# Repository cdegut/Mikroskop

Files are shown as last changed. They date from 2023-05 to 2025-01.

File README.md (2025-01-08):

# An open-sourced 3D printable microscope with a large CNC stage

[bioRxiv.org](https://www.biorxiv.org/content/10.1101/2024.12.31.630915v1)

Welcome to the repository for an affordable, high-performance, open-source microscope. Designed with researchers in mind, this versatile platform supports brightfield, fluorescence imaging, and high-throughput scanning of standard microtiter plates. It is fully 3D-printable, easy to assemble, and built for customization. Explore the project to access design files, firmware, and software, and join the growing community of users advancing accessible microscopy.

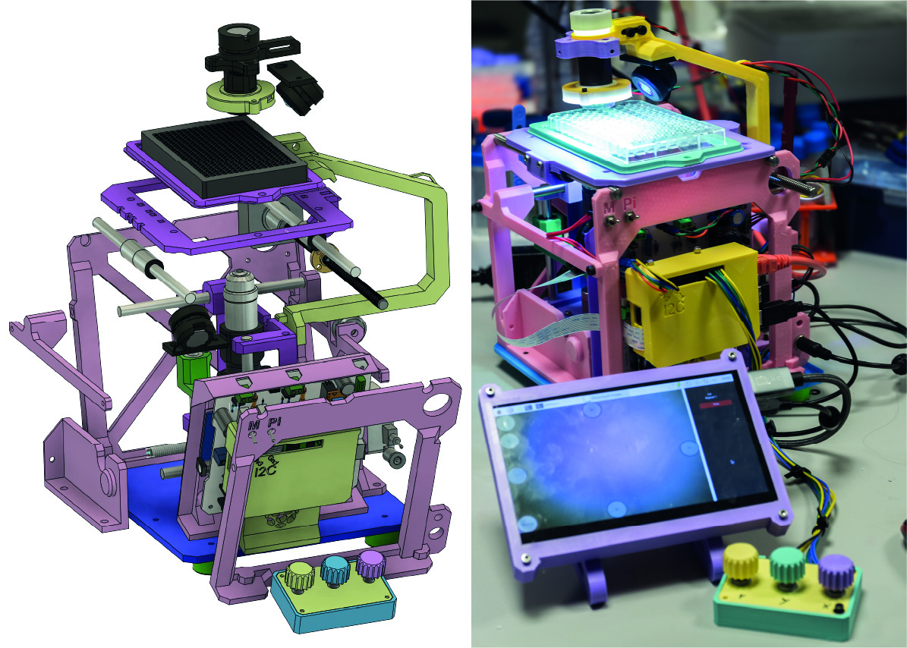
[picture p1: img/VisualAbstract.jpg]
Visual Abstract


A 200um tardigrade, 40x objective with  ring light for oblique illumination and Kristiansen type diffusion (magic tape above the sample!)

YouTube Video (https://www.youtube.com/watch?v=YF4frYpX1ZY)

## Navigation

[Building Instruction](hardware/readme.md)

[Bill of materials](hardware/)

[3D printable Files](hardware/print_files/readme.md)

[Samples images and video](samples)

[Arduino firmware](firmware/readme.md)

[Python sources](modules/readme.md)

Visit Stats

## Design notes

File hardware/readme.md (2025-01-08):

WIP expect everything to be dispnible by the 10th of january

This folder contains all the 3d printable files for building the microscope, with building instruction and some extra information in the readme files.

## Building order

[1 Base](mecanical_stage/base_plate/readme.md)

[2 X Axis](mecanical_stage/X_axis/readme.md)

[3 Optical Stack](optical_stack/readme.md)

[4 Focus Axis](mecanical_stage/Focus_axis/readme.md)

[5 Electronic](electronic/readme.md)

[6 Y Axis](mecanical_stage/Y_axis/readme.md)

[7 Raspberry Pi](raspberryPi/readme.md)

[8 Sample Illumination](mecanical_stage/Y_axis/readme.md)

[9 Sample holders](sample_holders)

## Bill of Materials

Bill Of meterials

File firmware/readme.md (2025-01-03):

# Arduino firmware

This is the arduino firmware, it should be uploaded on an Arduino R4 (minima) using the plateformIO extension for VScode.

## How to

Coming soon

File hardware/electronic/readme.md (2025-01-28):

# Electronic mainboard

The electronic main board mostly serves as an interconnect for off-the-shelf modules Power and control for the motors are managed by Trinamic TMC2209 stepper drivers in a StepStick-compatible format. While it is technically possible to use different drivers, the firmware employs the StallGuard4 feature of the Trinamic drivers for homing the axes. If a different driver is used, end-stop switches will need to be added, and the firmware reconfigured accordingly (not recomeended to try)
The current version 1.2.1 of the mainboard is slighly different from the figures, they will be updated in the coming days.

the gerber zip file contain all that is needed to order the PCB from a manufacturer such as JLCPCB. It is a 2 layer board with 1 oz/sq ft copper.

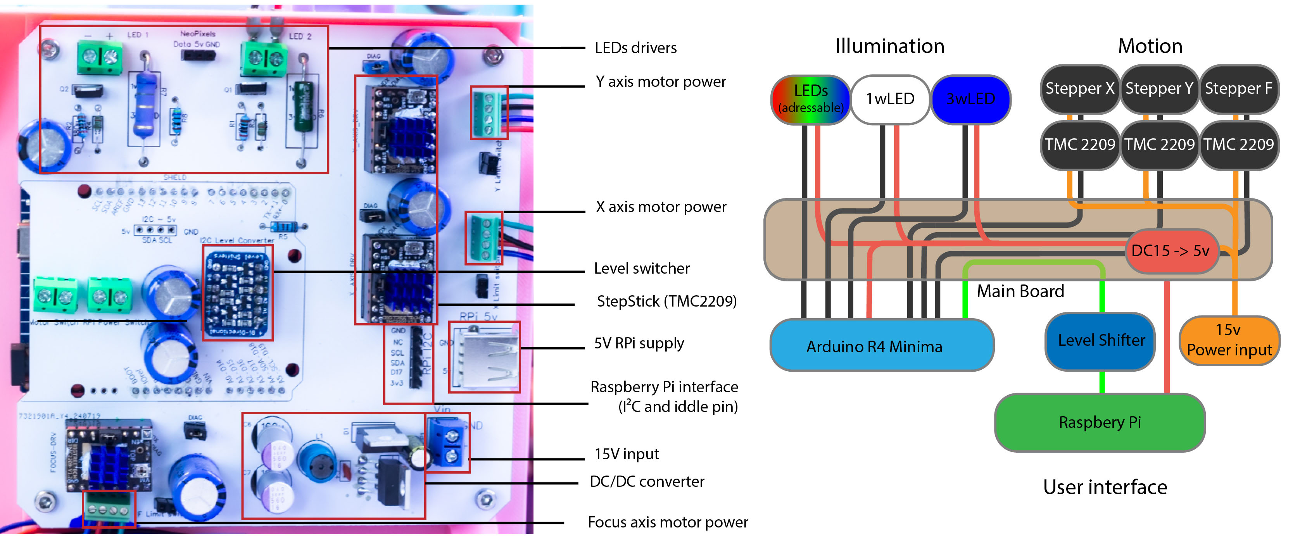
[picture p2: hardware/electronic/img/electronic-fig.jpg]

Photograph of the populated custom PCB and schematic of the interconnections. Red shows power line, black shows transistor to transistor logic (TTL), and green shows the I2C link.

The main printed part for the electronic is the electronic bracket that serve as a mount for all the electronic.
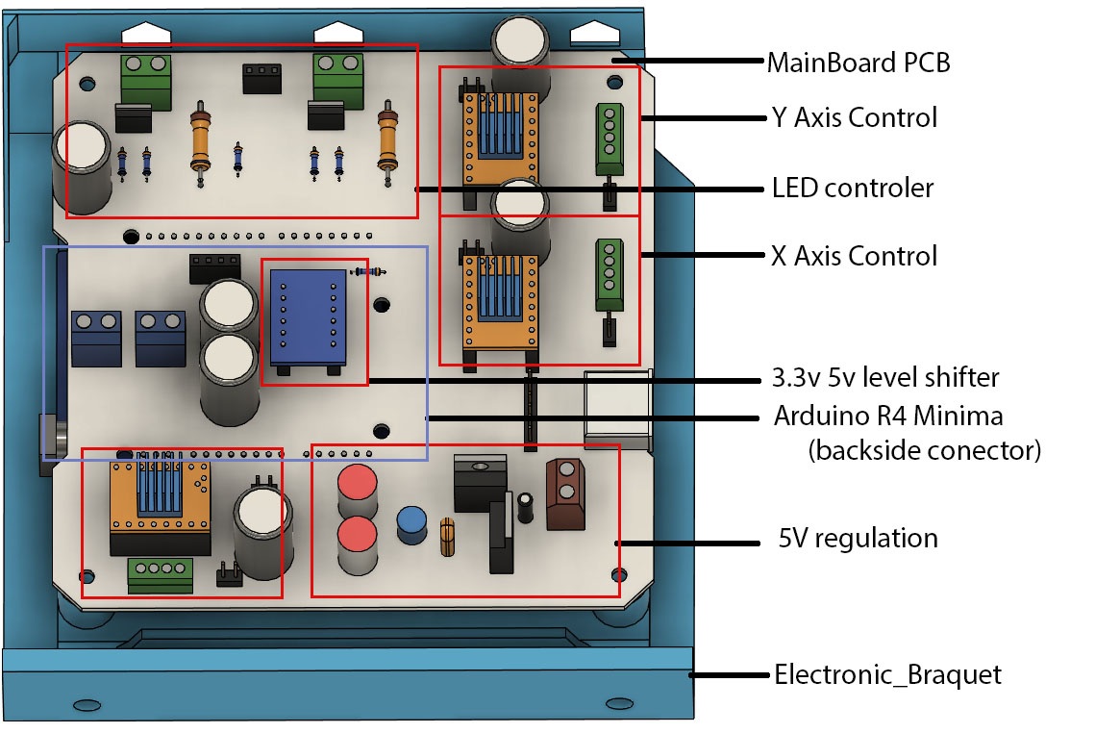
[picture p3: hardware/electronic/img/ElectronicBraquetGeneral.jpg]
General


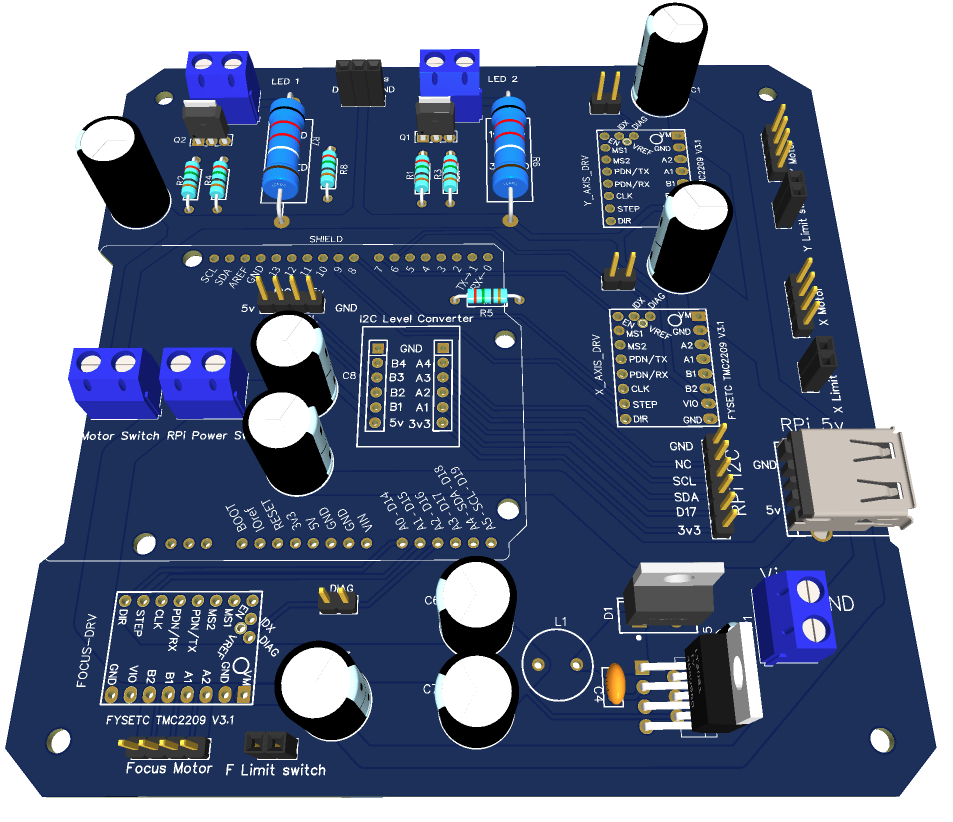
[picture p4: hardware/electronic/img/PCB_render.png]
PCB render

3D render of the PCB

PCB render
PCB Schematics

## Heat set inserts

The bracket requires:

* 2 - M4 ø 6 mm OD heat set insert
* 4 - M3 ø 5 mm OD heat set insert

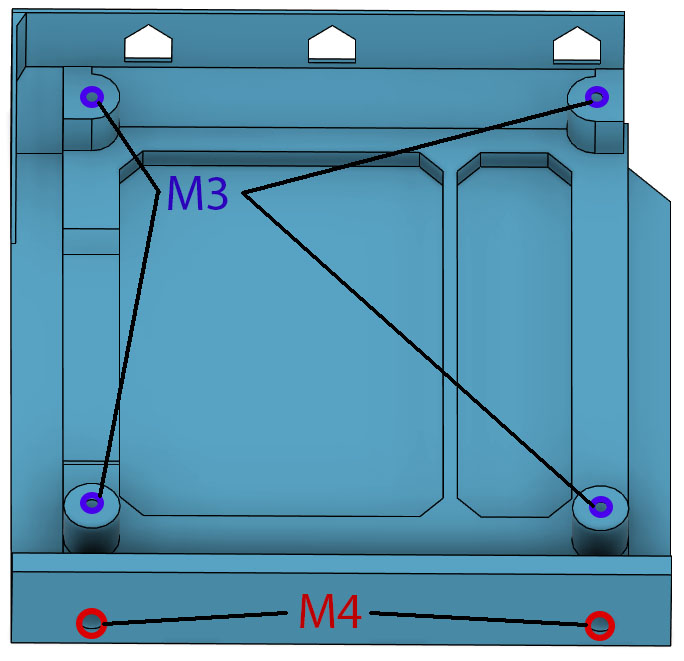
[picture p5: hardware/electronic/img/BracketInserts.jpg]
Inserts


## In Assembly context

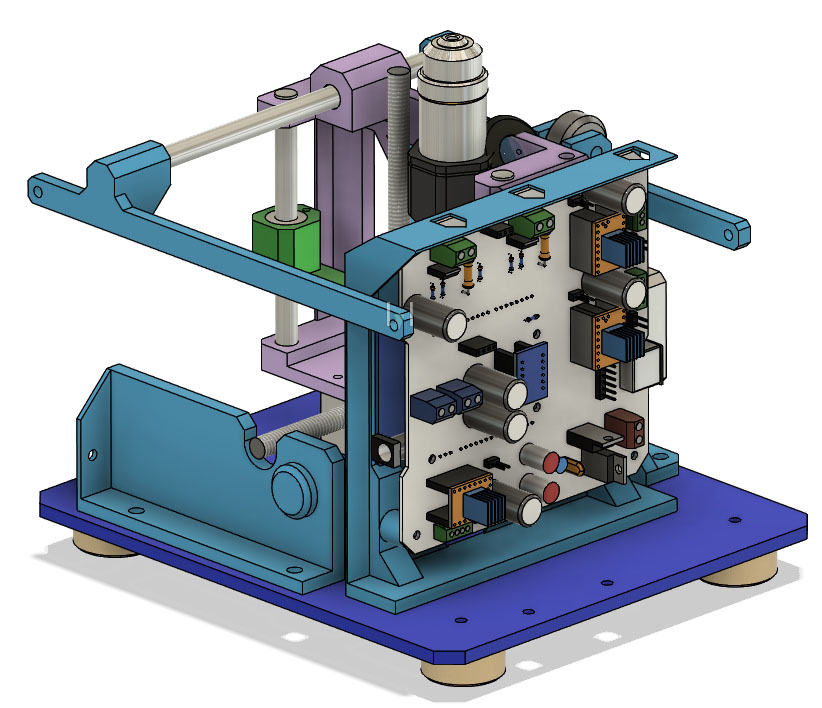
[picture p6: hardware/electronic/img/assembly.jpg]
Assembly


## Connection

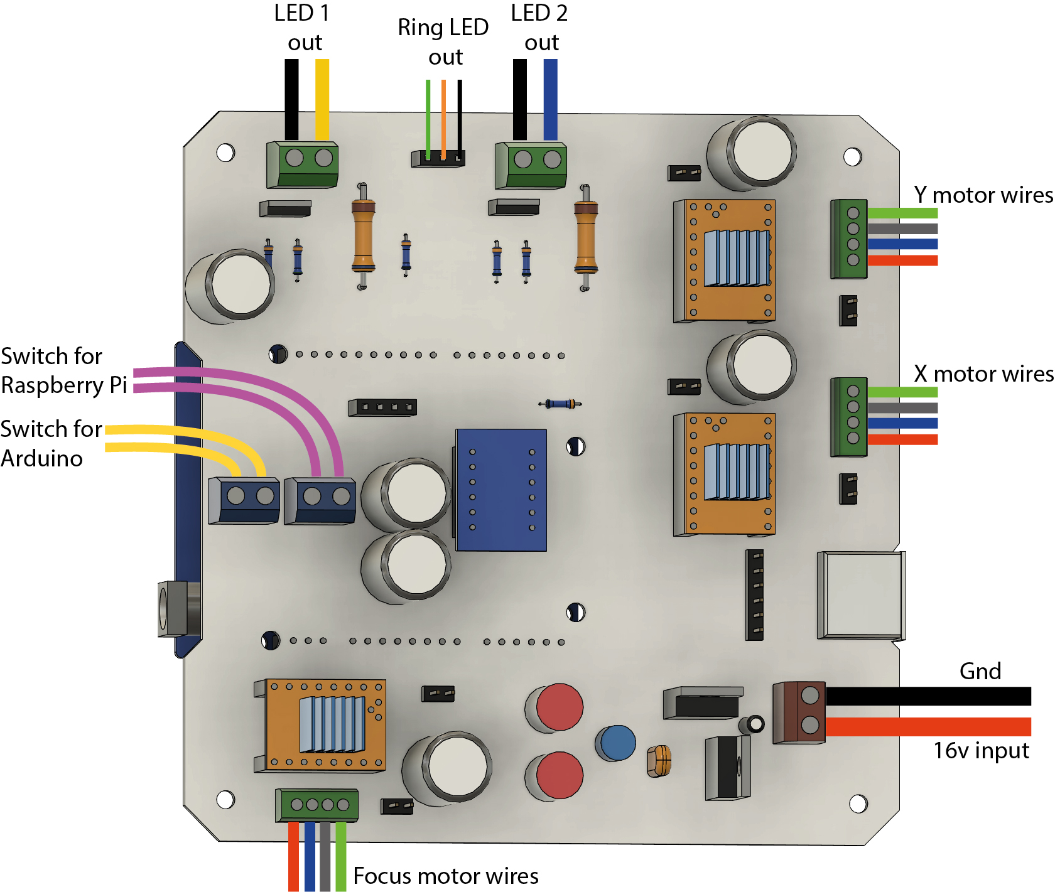
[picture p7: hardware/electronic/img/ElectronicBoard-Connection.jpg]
Connection image


## Alternate power supply

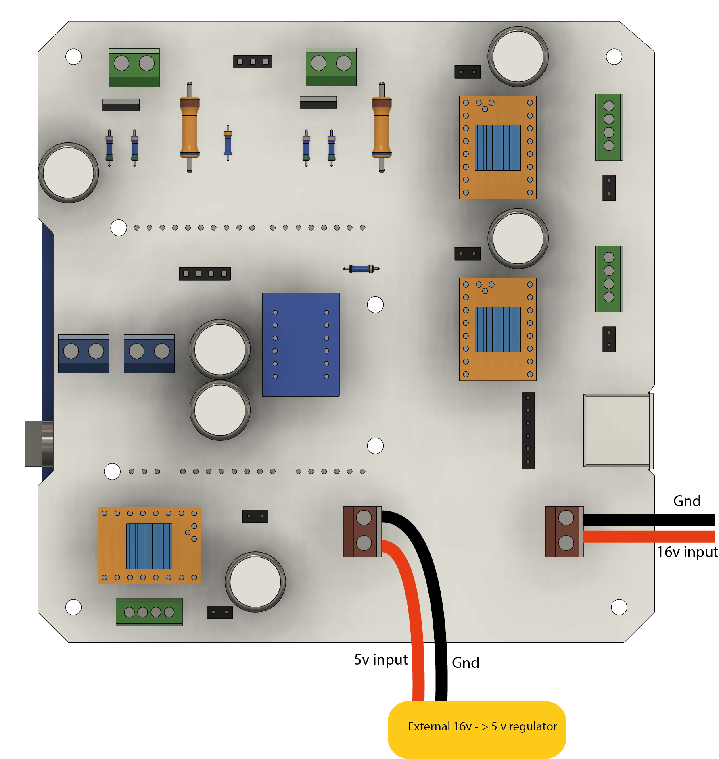
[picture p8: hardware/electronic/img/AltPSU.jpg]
External 5V


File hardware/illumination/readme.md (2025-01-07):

# Illumination system

The top illumination system is all attached to the light_snek , this part can be printed with large layer hight for speed (0.2mm), it is a structural part that should not flexed, therefore it should have >3 walls, and printed with >25% infill.

All the other parts contain threads, and like the optical stack, shopuld be printed with thin layers (<0.1mm), and highest possible quality setting.

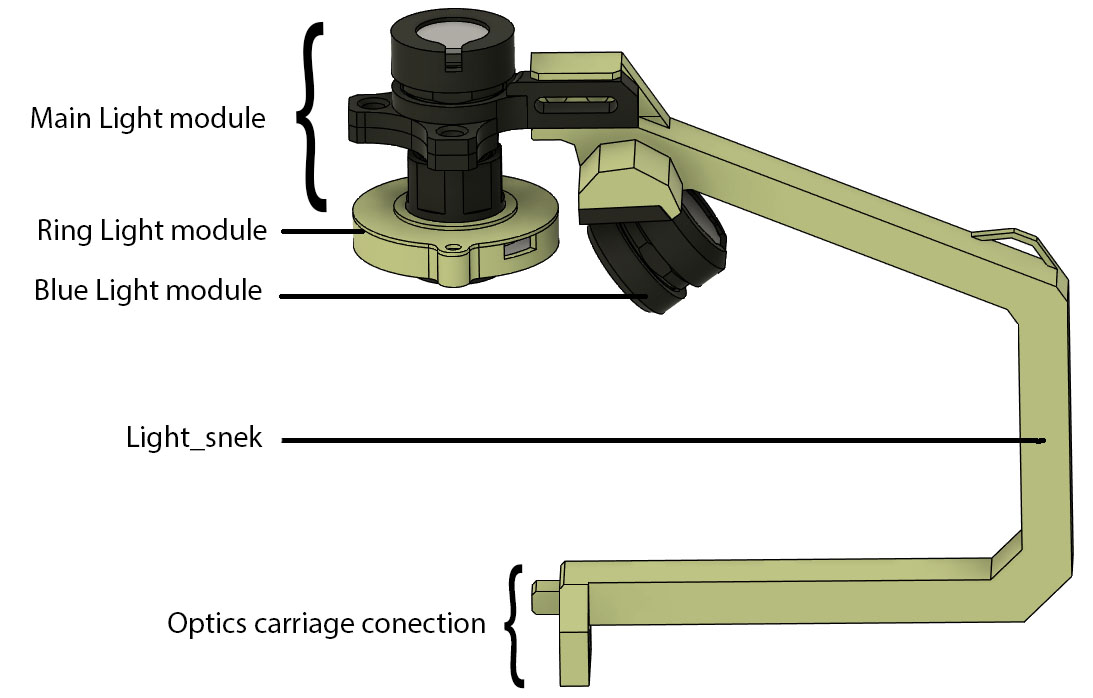
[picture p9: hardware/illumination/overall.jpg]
view of overall top side illumination


## Light Snek

The light snek is the large arm that connect the illumination system to the [optics carriage](../mecanical_stage/Focus_axis/readme.md).

## Illumination component

* [Main light Module](./main_light_module/readme.md)

* [Ring light Module](./ring_light_module/readme.md)

* [Blue light Module](./blue_light_module/readme.md)

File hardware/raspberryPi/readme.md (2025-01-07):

# The RaspberryPi

## Software configuration

[Raspberry Pi Software Configuration](RaspberryPi_config.md)

## Pi Bracket

A pi bracket and cover need to be printed.

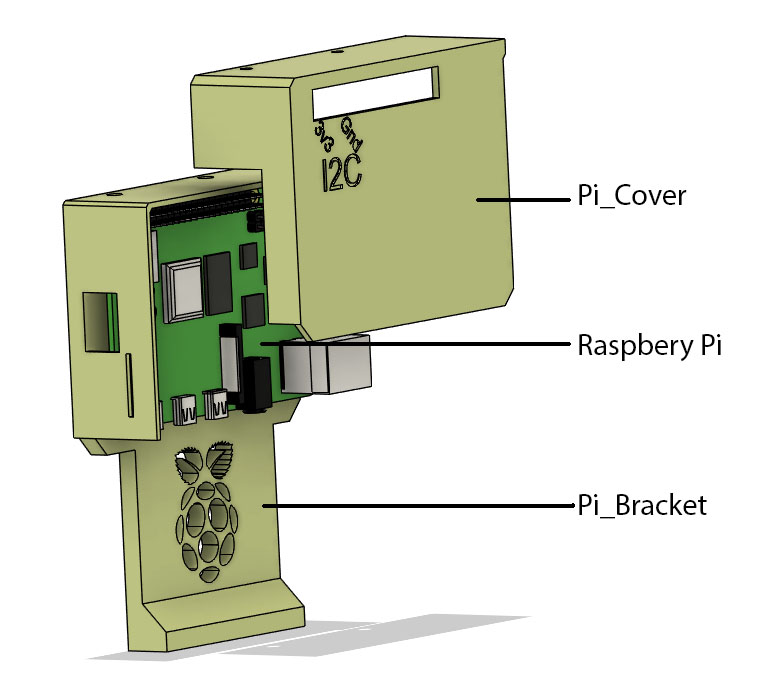
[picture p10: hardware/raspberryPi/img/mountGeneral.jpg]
general view


## Heat set inserts

This bracket use many inserts:

* 2 - M4 ø 6 mm OD heat set insert
* 2 - M3 ø 4 mm OD heat set insert
* 4 - M2 ø 4 mm OD heat set insert

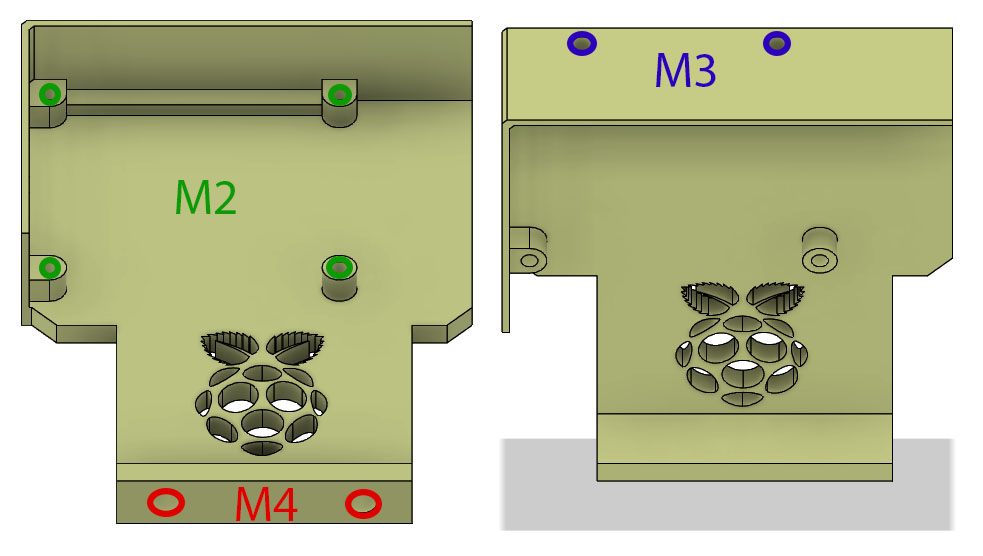
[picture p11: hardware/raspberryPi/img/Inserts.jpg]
Heat Set inserts


## I2C Connection

The I2C connection use 5 Female-Female Dupont style jumper wire. These can be bought either pre-made, or DIY with thin (26AWG) wire, and dupont crimping tool and connectors.

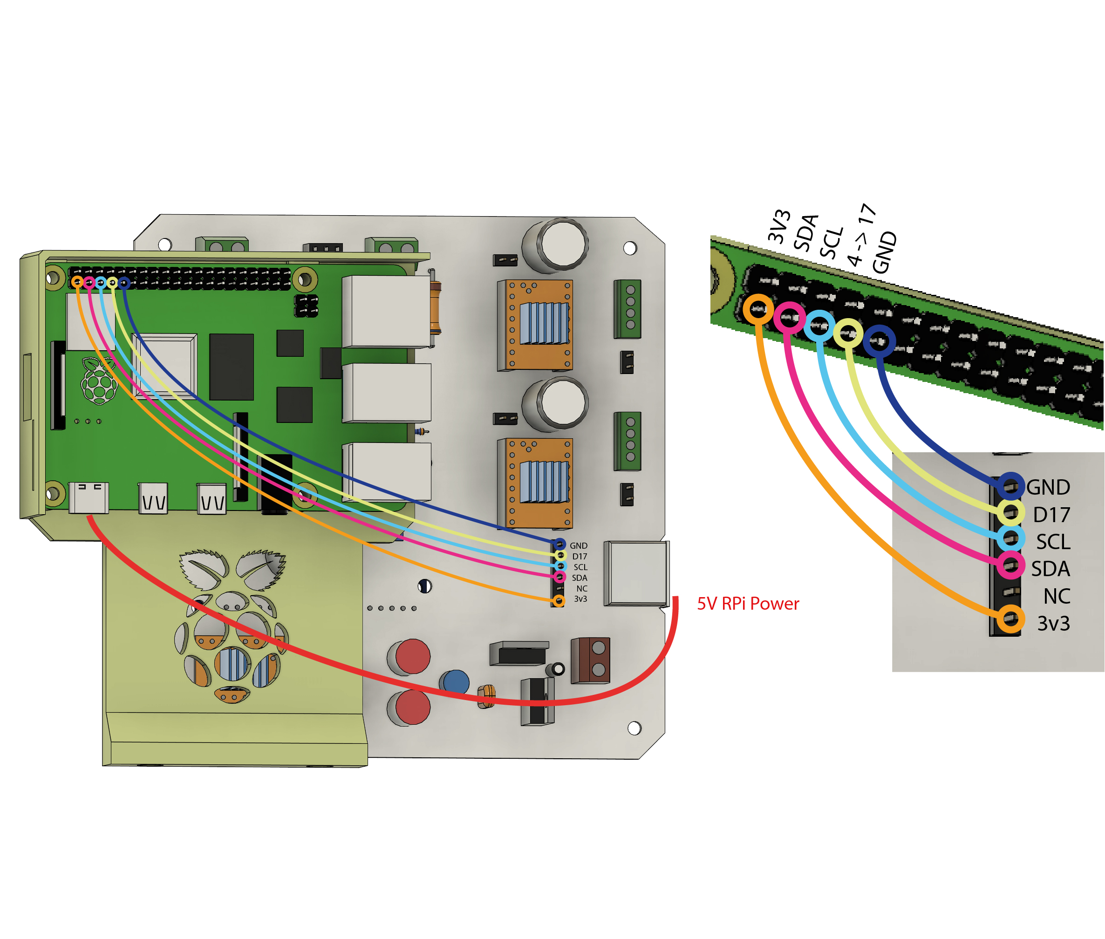
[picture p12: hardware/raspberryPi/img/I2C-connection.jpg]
I2C


## In Assembly context

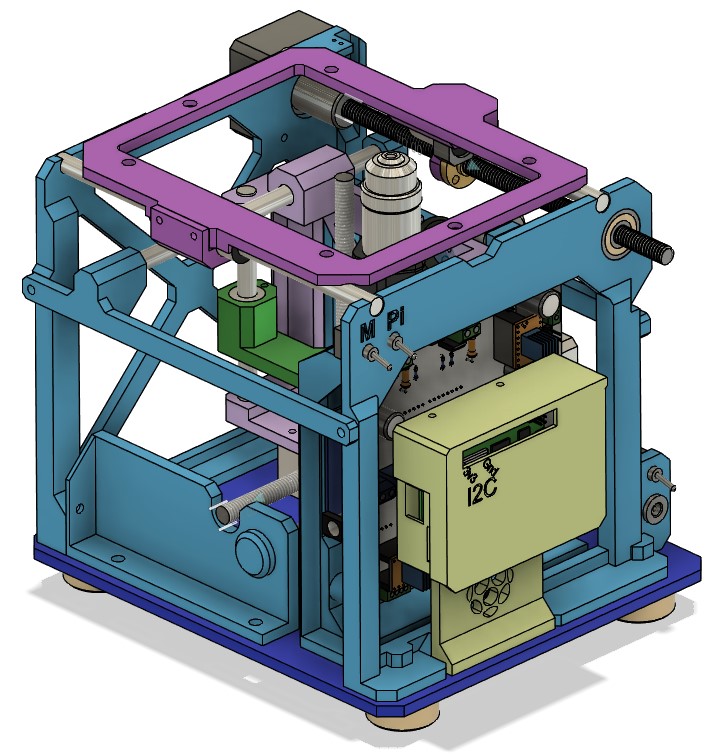
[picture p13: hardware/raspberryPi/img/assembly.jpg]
Assembly


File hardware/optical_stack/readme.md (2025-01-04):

# Optical Stack

Files for the optical stack, theses parts have threads and should therfore be **printed with thin layer (<0.1mm)** with the highest quality settings.

Scarf seams if present in your slicer will improve the thread quality.

**These part should be printed in black material.**

The main tube thread directly on the PiCamera C mount, this is metal on plastic and might need a litle bit of force.

Every lenses should have its own lens adapter printed so the very thin metal R.M.S. mount of the lens is threaded only once on plastic. Then the plastic/plastic of lens adapter and main tube can be attached and detached very easily with no domage to the threads.

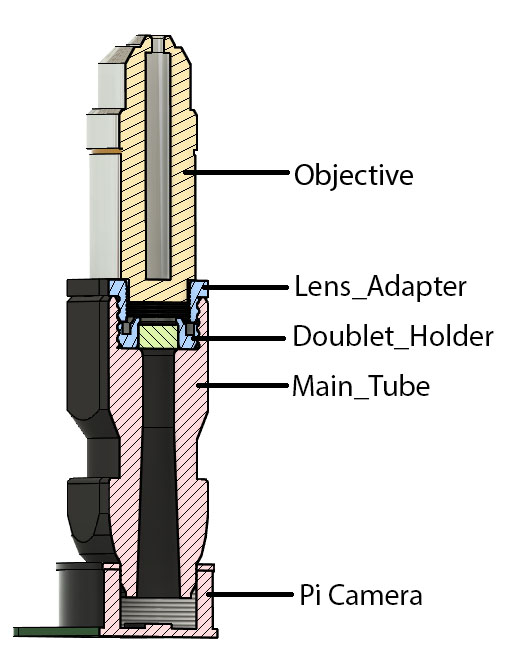
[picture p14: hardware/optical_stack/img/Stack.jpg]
full optical stack


The doublet tool is there to help threading the doublet holder (containing the doulbet) to the main tube:
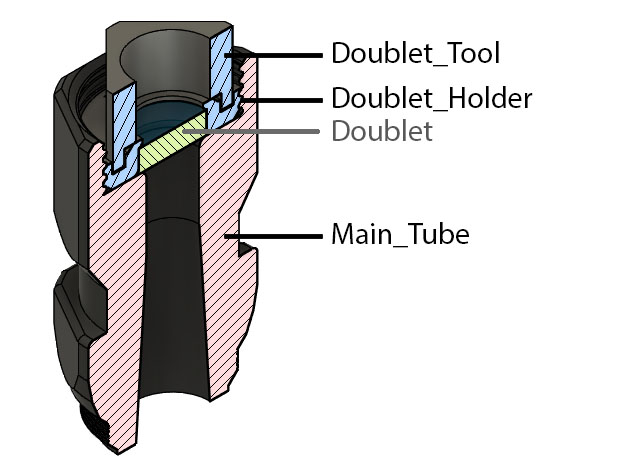
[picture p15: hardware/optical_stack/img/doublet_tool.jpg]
Use of doublet tool


Comparison of image qualityobtained using a 40X objective lens with and without the f50 doublet in the tube lens. Without condenser light (usually for lowmagnification work) the extra lens is not necessary. A substantial improvement in image quality is achieved when using the condenser (bottom right).
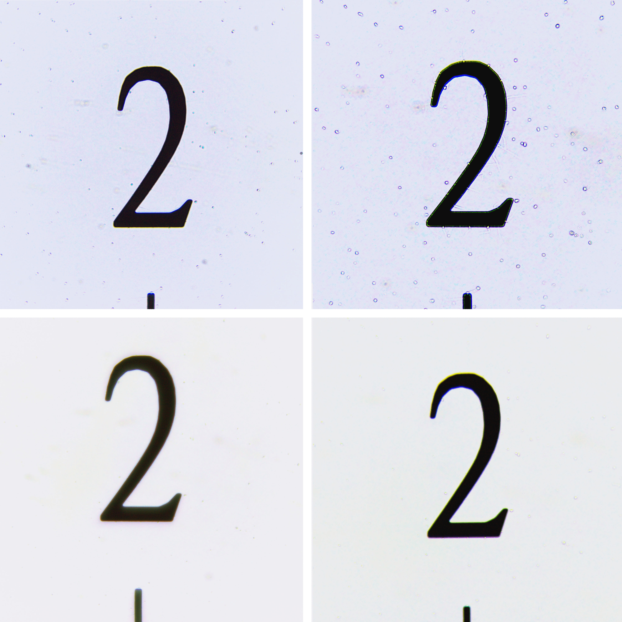
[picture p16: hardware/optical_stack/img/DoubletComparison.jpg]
Doublet comparison images


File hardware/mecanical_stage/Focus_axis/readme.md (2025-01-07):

# The focus carriage and axis

These parts are mounted on the X axis, and carry the optical stack

## General

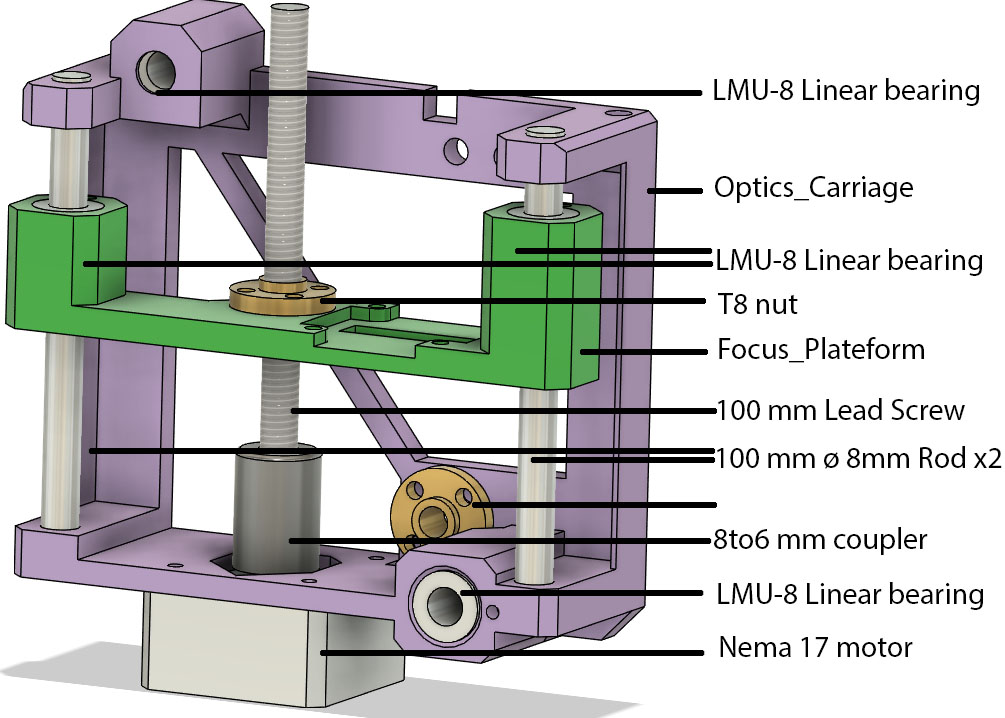
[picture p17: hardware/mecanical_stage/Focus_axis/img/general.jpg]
General view


## Bill of materials

* 2 - 100 mm ø 8 mm linear rods
* 1 - 100 mm ø 8 mm 2 mm pitch trapezoidal lead screw and nut
* 1 - 6 mm to 8 mm flexible shaft coupler
* 1 - Pancake NEMA 17 stepper motor
* 4 - LMU-8 8mm linear bearings

## Heat set inserts

* 3 - M4 ø 6 mm OD heat set insert
* 4 - M2 ø 4 mm OD heat set insert
Add the heat set insert:

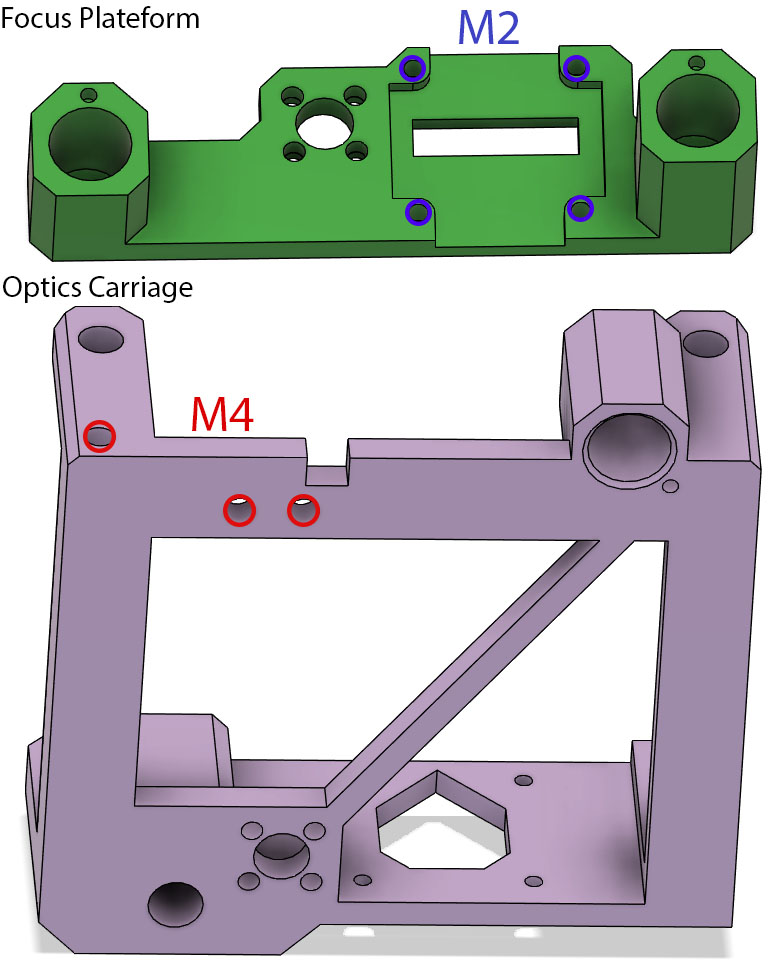
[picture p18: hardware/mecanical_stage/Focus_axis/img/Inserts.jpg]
Heat set inserts


## In Assembly context

Assemble all part and fit the [optical stack](../../optical_stack/readme.md):
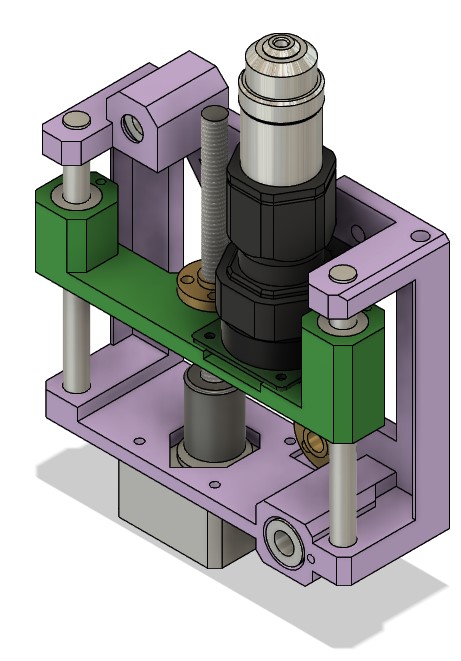
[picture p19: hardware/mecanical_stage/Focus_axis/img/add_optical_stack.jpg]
Add optical stack


Then fit on the X axis:
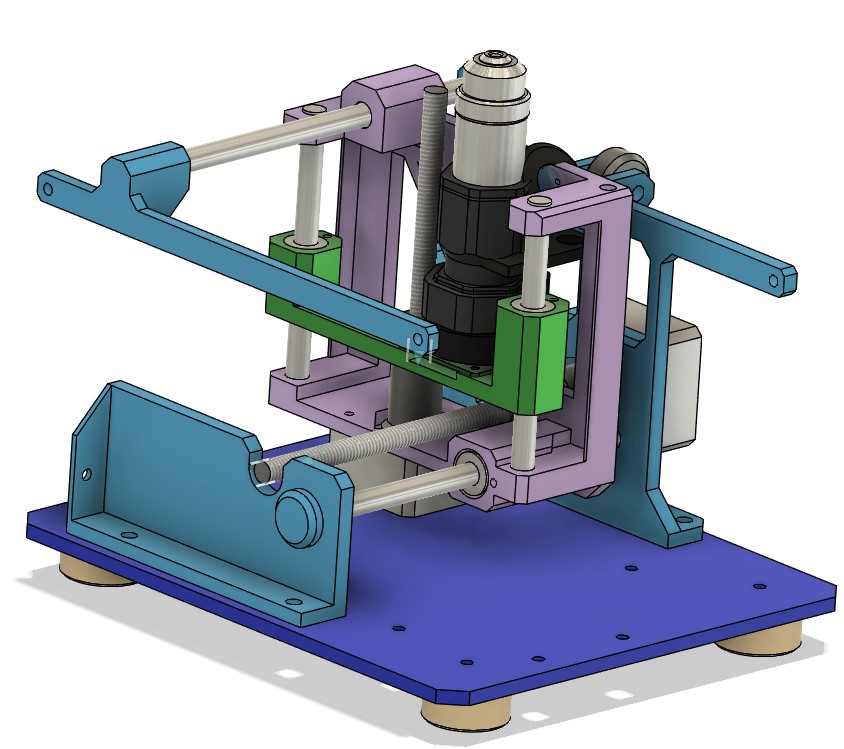
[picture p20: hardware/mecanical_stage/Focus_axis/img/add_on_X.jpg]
Add on X axis


## Off axis Blue LED

The [off axis blue LED](../../illumination/blue_light_module/readme.md) can be mounted on the optics carriage.
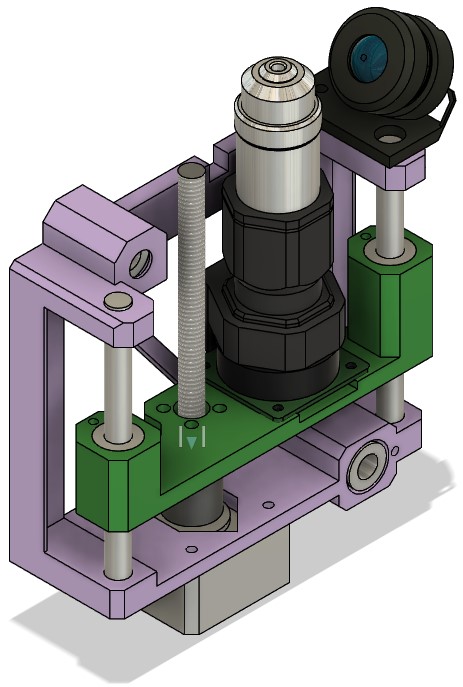
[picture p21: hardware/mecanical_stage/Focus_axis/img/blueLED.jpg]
Off axis blue


## Illumination connection

The [light snek](../../illumination/readme.md), holding the illumination system is going to be directly connected to the carriage:
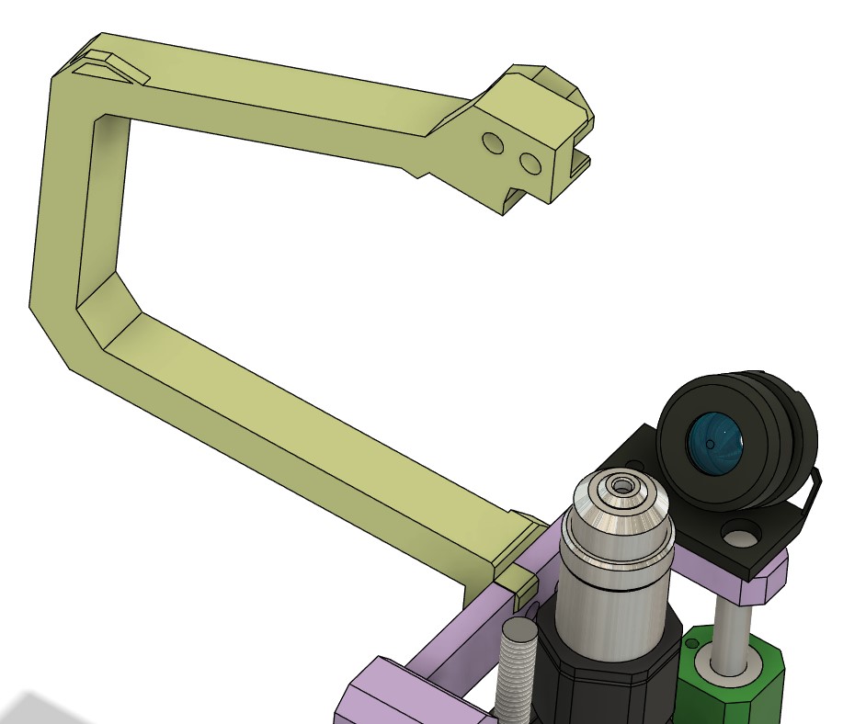
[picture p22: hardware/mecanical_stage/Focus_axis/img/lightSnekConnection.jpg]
Light Snek Connection


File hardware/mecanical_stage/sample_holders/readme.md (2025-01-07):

# Sample Holders

The microscope sample holders are attached to the stage withy two magnets 3x2
2 sample holders are provided:

* slide holder
* standard plate holder

Both have compliant mechanism to help lock the sample in place.

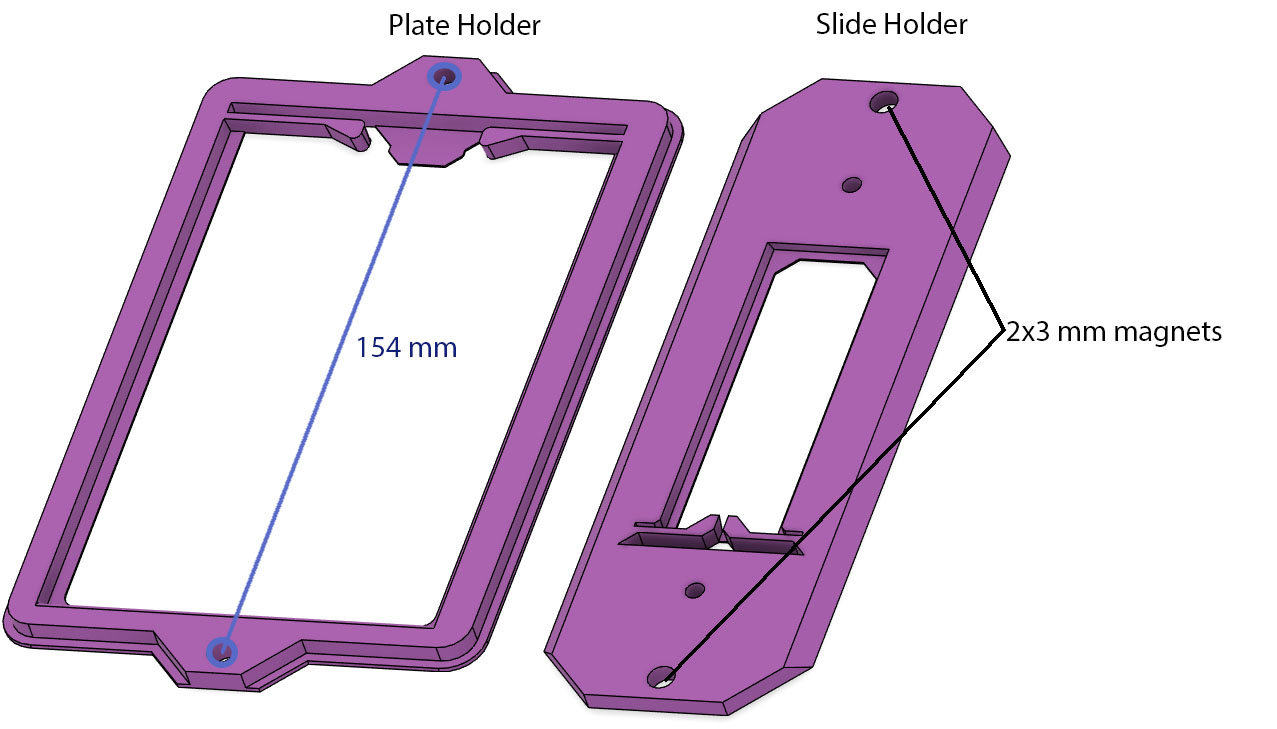
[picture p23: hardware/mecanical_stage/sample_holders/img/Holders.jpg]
Holder example


It is very simple to design your own sample holder for any shape sample, the only requirement is to have the two magnets holes 154 mm apart.

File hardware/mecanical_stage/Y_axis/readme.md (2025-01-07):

# The Y axis

The Y axis support and move the sample perpendicularly to the X axis.
It have 3 main printed parts, the back motor plate, the front panel and and a Y carriage.
Like all axis, the non printed part are 2 8 mm linear rods, a trapezoid lead screw and a NEMA 17 motor.
For increased stability the carriage use 3 LMU-8 linear bearings

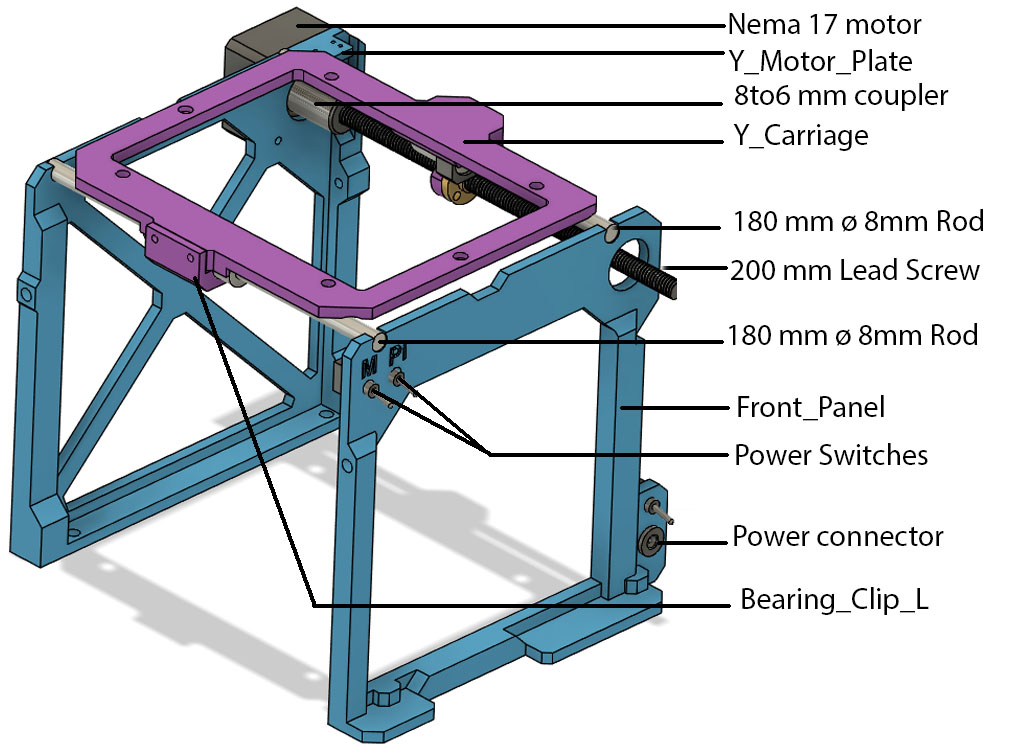
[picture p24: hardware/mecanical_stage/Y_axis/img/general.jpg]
General View


## Heat set insert

There is 4 M4  insert per panels

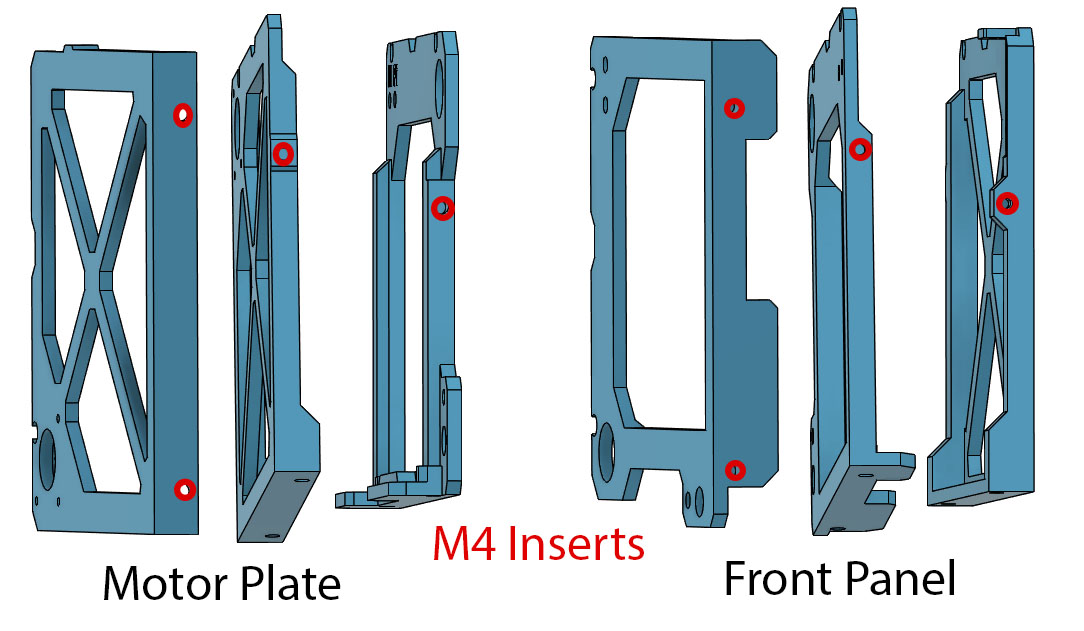
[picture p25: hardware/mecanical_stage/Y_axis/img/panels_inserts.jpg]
Panels inserts


2 M3 inserts on the Y carriage to fit the bearing clip

Carriage insert

## Bill of materials

* 2 - 180 mm ø 8 mm linear rods
* 3 - LMU-8 Linear bearings
* 1 - 200 mm ø 8 mm 2 mm pitch trapezoidal lead screw and nut
* 1 - 6 mm to 8 mm flexible shaft coupler
* 1 - Pancake NEMA 17 stepper motor
* 8 - M4 ø 6 mm OD heat set inserts
* 2 - M3 ø 4 mm OD heat set inserts

## In Assembly context

assembly

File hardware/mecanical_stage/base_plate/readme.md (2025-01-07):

# Base Plate and Feets

The base plate is designed to bu laser cut from 5 mm acrylic, but can also be 3D printed in standard PLA. It is provided as both DXF file and 3mf.

The feet can be printed in PLA, but printing in TPU will greatly improve stage stability.

Base Plate and Feet

# Files

* [Base Plate](Base_Plate_V1.3mf)
* [Feet](Feet_V1.3mf)

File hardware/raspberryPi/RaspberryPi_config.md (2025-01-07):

# Raspberry pi config

These are specific configurations needed for the Raspberry Pi to work well with the microscope.

all these change need to be made in

## in /boot/firmware/config.txt

### I2C

Mandatory change

```bash
# activate I2C interface
dtparam=i2c_arm=on
# Clock stretching by slowing down to 10KHz
dtparam=i2c_arm_baudrate=10000
```

### Screen configuration

if using MPI7002, 7" 1024x600 touch screen; change:

```bash
dtoverlay=vc4-kms-v3d
```

to

```bash
dtoverlay=vc4-fkms-v3d
```

and at the end add:

```bash
# Allow for 1024x600 resolution do not add if using different screen
hdmi_group=2
hdmi_mode=87
hdmi_cvt 1024 600 60 6 0 0 0
hdmi_drive=1
```

## Packages to install

upgrade pip and install the needed packages:

```bash
pip install --upgrade pip setuptools wheel smbus2 customtkinter packaging opencv-python --break-system-packages
sudo apt install python3-rpi-lgpio
```

## Increase Swap size

Strongly suggest to increase the size of the Swap file:

run these two commands:

```bash
sudo dphys-swapfile swapoff
sudo nano /etc/dphys-swapfile
```

then change:

```bash
CONF_SWAPSIZE=100
```

to

```bash
CONF_SWAPSIZE=2048
```

And run again these:

```bash
sudo dphys-swapfile setup
sudo dphys-swapfile swapon
```

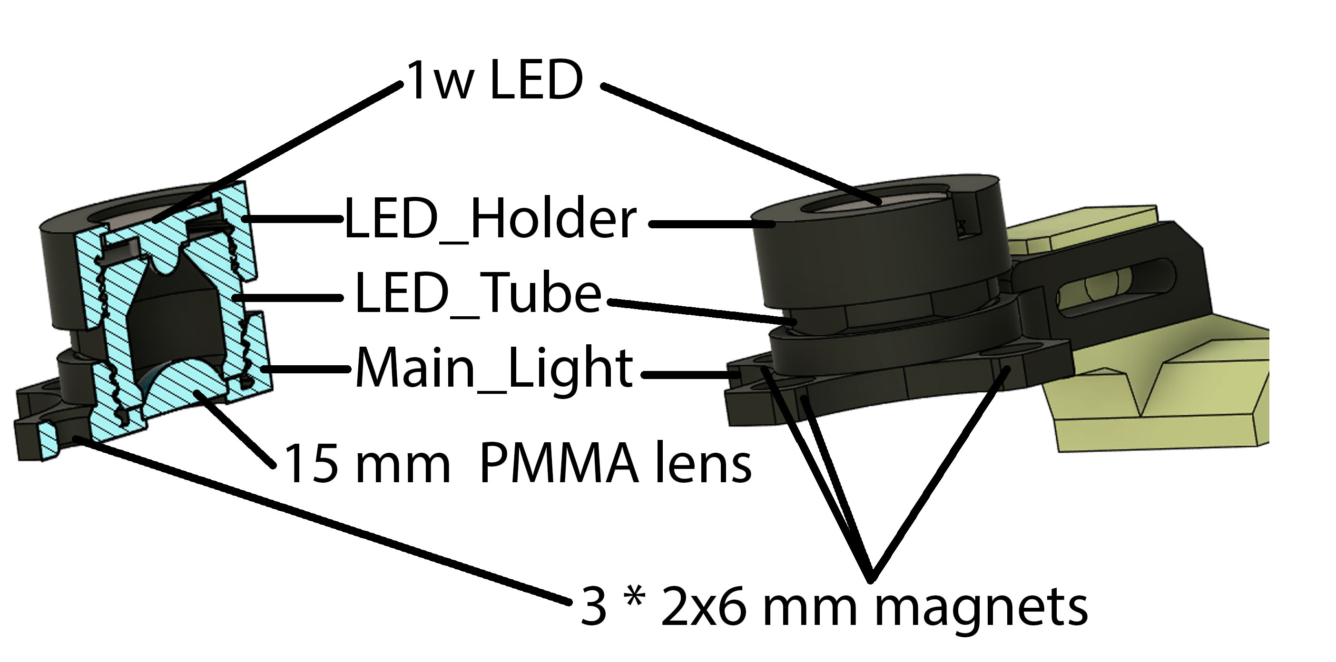
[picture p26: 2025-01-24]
hardware/illumination/main_light_module/img/mainLight.jpg

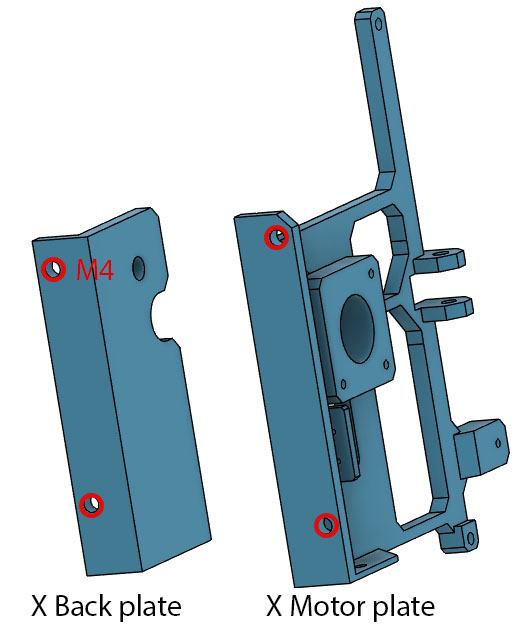
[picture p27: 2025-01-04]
hardware/mecanical_stage/X_axis/img/insert.jpg

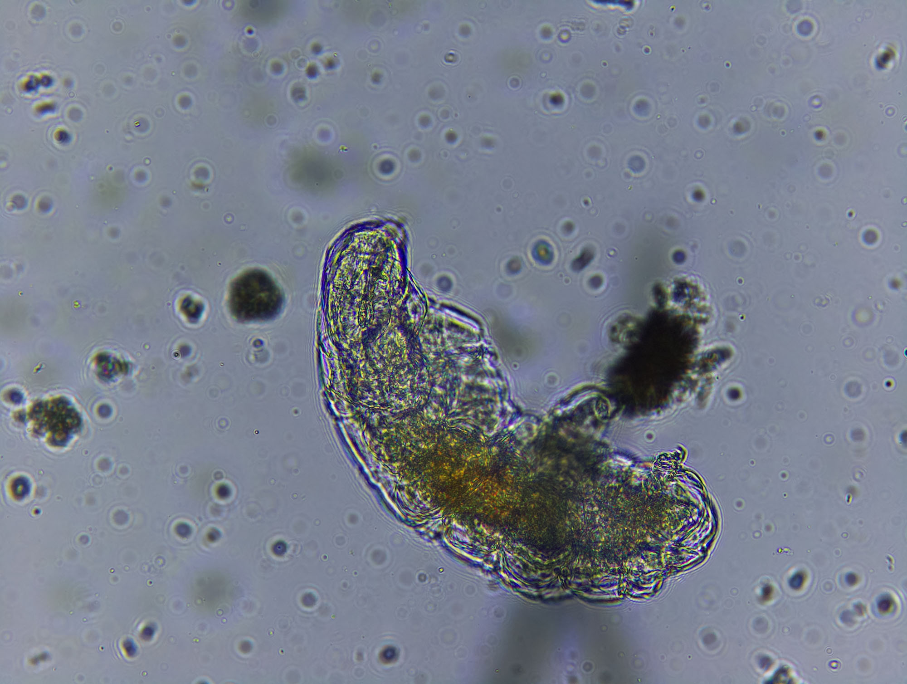
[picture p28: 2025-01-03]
hardware/illumination/main_light_module/img/Tardigrade_woCondenser.jpg

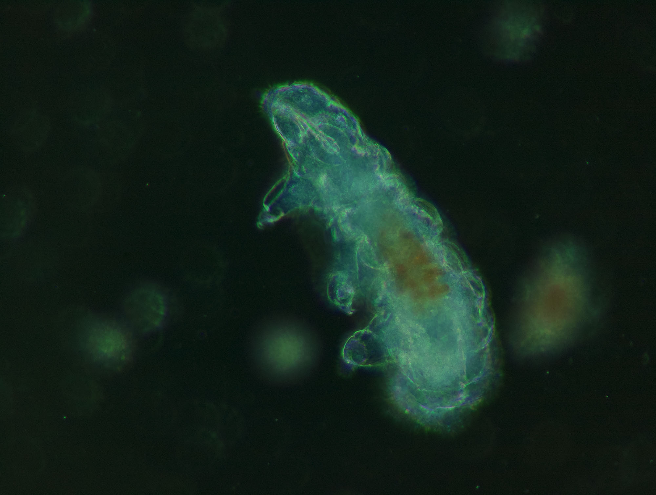
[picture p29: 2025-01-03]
hardware/illumination/ring_light_module/img/DarkField.jpg

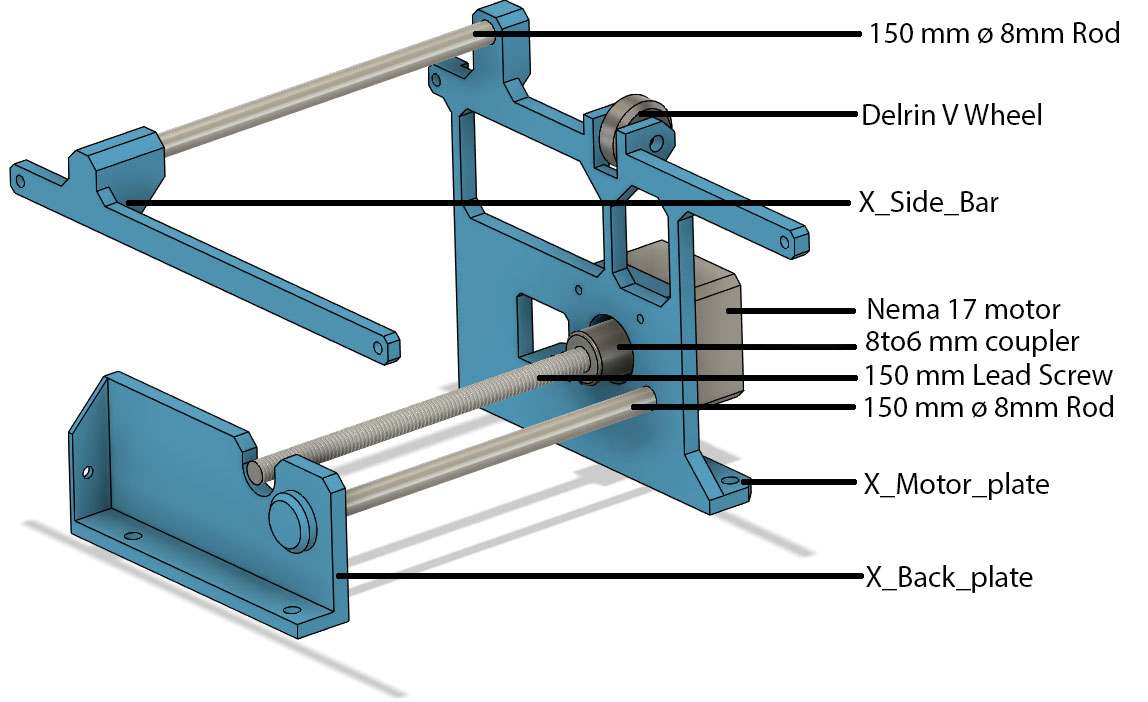
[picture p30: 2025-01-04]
hardware/mecanical_stage/X_axis/img/general.jpg

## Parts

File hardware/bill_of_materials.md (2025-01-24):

**WIP**
|   Amount  | Description | Buying link 1 | Aliexpress |
|:---------:|-------------|---------------|------------|
|           | **TOOLS**   |
|    1      | Soldering Iron and wire | [Amazon.co.uk](https://www.amazon.co.uk/YIHUA-Digital-Soldering-Lead-Free-Calibration/dp/B0CMQHYTK5)| [B Sets](https://www.aliexpress.com/item/1005006240211620.html)  |
|    1      | Heat set insert tool (not necessary but very usefull) | [Amazon.co.uk for YIHUA iron](https://www.amazon.co.uk/Kigniote-Heat-set-Soldering-Threaded-Compatible/dp/B0CXPQBFH8) | [For T12](https://www.aliexpress.com/item/1005008028914537.html) [Standalone](https://www.aliexpress.com/item/1005005979413935.html)|
|    1      | Crimping tool, can be skipped, but necessary for making the joystick wire| [Amazon.co.uk](https://www.amazon.co.uk/Taiss-Ratcheting-Connector-SN-28B-Crimping/dp/B0BYMT2BRP) | [AliExpress](https://www.aliexpress.com/item/1005004496428442.html)|
|           | **MOTION SYSTEM**   |                            
|   2       | 100 mm ø 8 mm linear rods | [Amazon.co.uk](https://www.amazon.co.uk/Linear-Diameter-Hardened-Straight-Bearing/dp/B0B5W76XVB) | [AliExpress](https://www.aliexpress.com/item/1005006293171727.html)|
|   2       | 150 mm ø 8 mm linear rods |[Amazon.co.uk](https://www.amazon.co.uk/Linear-Diameter-Hardened-Straight-Bearing/dp/B0B5W76XVB) | [AliExpress](https://www.aliexpress.com/item/1005006293171727.html)|
|   2       | 180 (200) mm ø 8 mm linear rods |[Amazon.co.uk](https://www.amazon.co.uk/Linear-Diameter-Hardened-Straight-Bearing/dp/B0B5W76XVB) | [AliExpress](https://www.aliexpress.com/item/1005006293171727.html)|
|   5       | LMU8UU 8mm linear bearings | [Amazon.co.uk](https://www.amazon.co.uk/sourcing-map-Bearings-Bearing-Printer/dp/B0CNCQMYTG) | [AliExpress](https://www.aliexpress.com/item/1005004774546723.html)|
|   1       | 100 mm ø 8 mm 2 mm pitch trapezoidal lead screw and nut| [Amazon.co.uk](https://www.amazon.co.uk/sourcing-map-Stainless-Copper-Printer/dp/B07QXJDKCK) | [AliExpress Lead 2mm](https://www.aliexpress.com/item/1005003720855082.html)|
|   1       | 150 mm ø 8 mm 2 mm pitch trapezoidal lead screw and nut| [Amazon.co.uk](https://www.amazon.co.uk/sourcing-map-Stainless-Copper-Printer/dp/B07R1W6MCT)| [AliExpress Lead 2mm](https://www.aliexpress.com/item/1005003720855082.html)|
|   1       | 200 mm ø 8 mm 2 mm pitch trapezoidal lead screw and nut| [Amazon.co.uk](https://www.amazon.co.uk/sourcing-map-uxcell-Stainless-Printer/dp/B07QYLW15S)| [AliExpress Lead 2mm](https://www.aliexpress.com/item/1005003720855082.html) |
|   3       | 6 mm to 8 mm flexible shaft coupler| [Amazon.co.uk](https://www.amazon.co.uk/sourcing-map-Aluminum-Coupling-Connector/dp/B09139YZ2H) | [Aliexpress](https://www.aliexpress.com/item/1005006305848755.html) |
|   3       | Pancake NEMA 17 (42 x 23 mm) stepper motor|[Amazon.co.uk](https://www.amazon.co.uk/SIMAX3D-stepper-degrees-Creality-extruder/dp/B08FFM6LRL) | [17HS4023](https://www.aliexpress.com/item/1005006005430638.html) |
|   1       | Derlin Wheel|[Amazon.co.uk](https://www.amazon.co.uk/sourcing-map-Printer-Bearing-Plastic/dp/B0DPL2N6K7) | [Aliexpress Big](https://www.aliexpress.com/item/1005004275676552.html) |
|           | **STRUCTURE** |
|   500g    | Black PLA for the optics|||
|   1kg     | PLA for the structure || |
|    tbd    | M2 ø 3.2 mm OD heat set insert |[Amazon.co.uk](https://www.amazon.co.uk/Coptiner-M2x4x3-2mm-Embedment-Threaded-Internal/dp/B0D99SLDTQ) |
|    tbd    | M3 ø 4.5 mm OD heat set insert|[Amazon.co.uk]() | [Aliexpress](https://www.aliexpress.com/item/1005003582355741.html) |
|    tbd    | M4 ø 6 mm OD heat set insert|[Amazon.co.uk]() | [Aliexpress](https://www.aliexpress.com/item/1005003582355741.html) |
|    1      | kit of M2 M3 M4 screws |[Amazon.co.uk](https://www.amazon.co.uk/1080pcs-Stainless-Washers-Machine-Assortment/dp/B0C8TBJZJ1) |
|           | ** OPTICS ** |
|   1       | *f50* ø = 12.7 mm (1/2 inch) achromatic doublet |[ThorLabs](https://www.thorlabs.com/thorproduct.cfm?partnumber=AC127-050-A) | [Aliexpress](https://www.aliexpress.com/item/1005007663163643.html) |
|   3       | 15 mm PMMA lens |[Amazon.co.uk](https://www.amazon.co.uk/PATIKIL-Diameter-Condenser-Flashlight-Transparent/dp/B0BR5PMGWD) | [Aliexpress](https://www.aliexpress.com/item/1005006610294774.html) |
|   1       | 250x250x5 mm perspex plate *if laser cutting is possible* |   
|           | **LIGHT** |
|   1       | 1 W white LED mounted on star heatsink |
|   6       | 2 x 6 mm Neodymium magnets for the condenser|
|   2 + x2  | 2 x 6 mm Neodymium magnets for the condenser for sample holder (2 + 2 per holders) |
|   1       | <span style="color:blue"> 3 W blue LED mounted on star heatsink  </span>|
|   1       | <span style="color:blue"> **OR** 1 W blue LED mounted on star heatsink  </span>|
|   100g    | <span style="color:blue"> PETG or heat resistant plastic (not needed for 1W option)  </span>|
|   1       | kit 26 AWG silicon insulation flexible wire | [Amazon.co.uk](https://www.amazon.co.uk/Silicone-Electrical-Wire-HuLuWa-Stranded-Aircraft/dp/B0C8HPNV8Y) | [AliExpress](https://www.aliexpress.com/item/1005007256968315.html) |
|   1       | 16xRGB LED Ring light | [The Pi Hut](https://thepihut.com/products/adafruit-neopixel-ring-16-x-5050-rgb-led-with-integrated-drivers) | [AliExpress](https://www.aliexpress.com/item/1005002287819725.html) |
|           | **CONTROL** |
|   1       | Raspberry Pi HQ Camera C - mount | [The Pi Hut](https://thepihut.com/products/raspberry-pi-high-quality-camera-module) | N.A. |
|   1       | Raspberry Pi 4 4Gb |  [The Pi Hut](https://thepihut.com/products/raspberry-pi-4-model-b?variant=20064052740158) | N.A. |
|   1       | SD Card > 32Gb | [Amazon.co.uk](https://www.amazon.co.uk/SanDisk-256GB-Ultra-microSDXC-Adapter/dp/B0B7NV73PJ) | N.A. |
|   1       | 200 mm Flex Cable for Raspberry Pi Camera |  [The Pi Hut](https://thepihut.com/products/flex-cable-for-raspberry-pi-camera-or-display-200mm-8) | |
|   1       | Arduino R4 Minima | [The Pi Hut](https://thepihut.com/products/arduino-uno-r4-minima) | [AliExpress](https://www.aliexpress.com/item/1005008070945257.html) |
|   5       | Female-Female dupont wire for I2C |
|   1       | 16V Power supply | [Amazon.co.uk](https://www.amazon.co.uk/KFD-Keyboard-PSR-2000-PSR-S900-Workstation/dp/B07B9GDY4P)
|           | **MAIN BOARD** |
|   1       | Main PCB       | Upload files to [JLCPCB](https://jlcpcb.com/) ||
|   3       | TMC 2209 stepstick module stepper driver | [Amazon.co.uk](https://www.amazon.co.uk/BIQU-DIRECT-Printer-Stepstick-Heatsink/dp/B07ZCTRS6N) | [AliExpress](https://www.aliexpress.com/item/33028050145.html)
|   1       | Adafruit 3.3v <-> 5v 12C safe logic level converter | [The Pi Hut](https://thepihut.com/products/adafruit-4-channel-i2c-safe-bi-directional-logic-level-converter)
|   2       | Waveshare DC-DC Buck Mini Module 6-36V to 5V 4A ***PCB version 1.2*** | [The Pi Hut](https://thepihut.com/products/dc-dc-buck-mini-module-3-3v-5v) ||
|   **OR** 2| Mini 560 -5V buck converter ***PCB version 1.2*** || [AliExpress 5V vers](https://www.aliexpress.com/item/1005002525645136.html)  |
|   6       | 1000 µf Electrolytic capacitor |
|   2       | IRLU024NPBF |
|   2       | 10kΩ resistor |
|   2       | 180Ω resistor |
|   1       | 1kΩ resistor |
|   1       | 480Ω resistor |
|   1       | 6.8R 1W resistor per 1W LED |
|   1       | 2R 3W resistor per 3W LED |
|   3       | Switch
|   5       | Through hole 2 poles 5.08 mm pitch screw terminal block for power connections
|   3       | Through hole 4 poles 2.54 mm pitch screw terminal block for motor wires
|   1       | Through hole 90° Female USB type A socket
|   6       | 1x8 2.54 mm PCB female pin headers for TMC drivers socket
|   3       | 1x2 2.54 mm PCB female pin headers for TMC drivers socket
|   2       | 1x6 2.54 mm PCB female pin headers for I2C level converter socket
|   OR 3    | 1x32 2.54 mm PCB female pin headers (will need cutting)
|   2       | 1x32 2.54 mm PCB breakable male pin headers for Arduino and I2C connector
|  either 1 | Ring LED connector: Through hole 3 poles 2.54 mm pitch screw terminal block
|  or 1     | Ring LED connector: 1x3 2.54 mm PCB female pin headers if you have a dupont wire  crimping tool

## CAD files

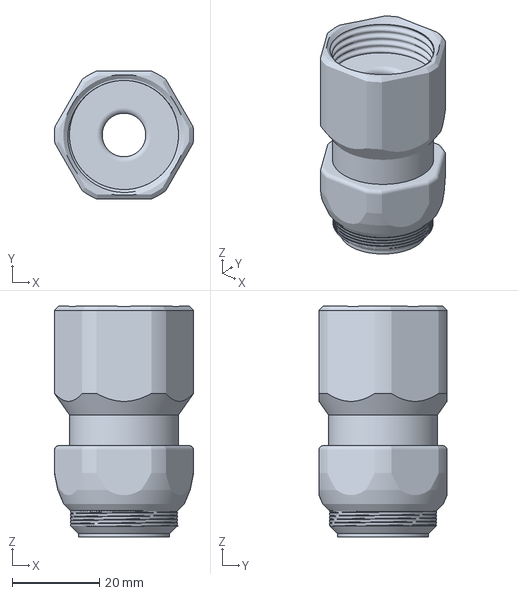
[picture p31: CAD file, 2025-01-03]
hardware/optical_stack/Main_Tube_V1.3mf
32.0 x 29.4 x 53.1 mm

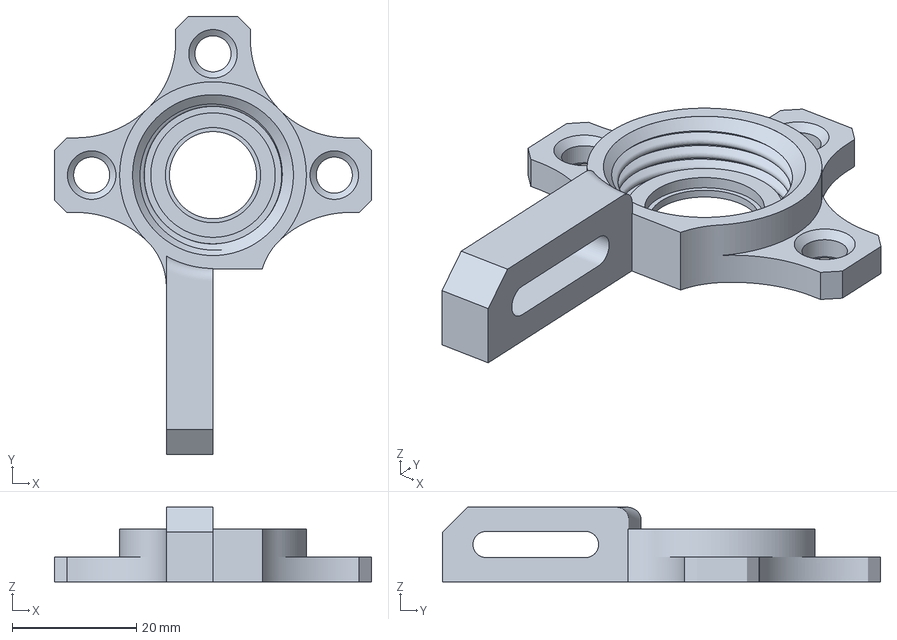
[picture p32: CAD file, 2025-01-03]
hardware/illumination/main_light_module/Main_light.3mf
51.0 x 70.4 x 12.0 mm

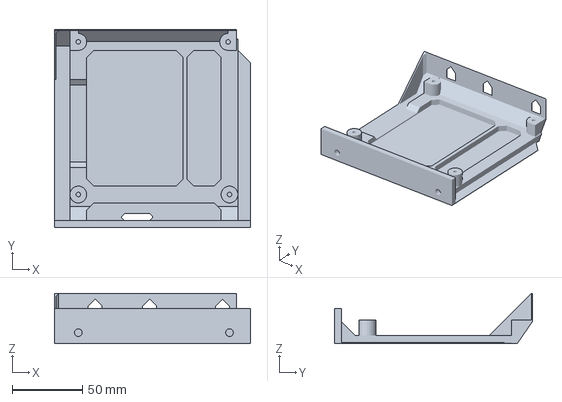
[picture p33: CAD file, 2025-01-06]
hardware/electronic/Electronic_Bracket_V1.3mf
140.0 x 141.7 x 35.8 mm

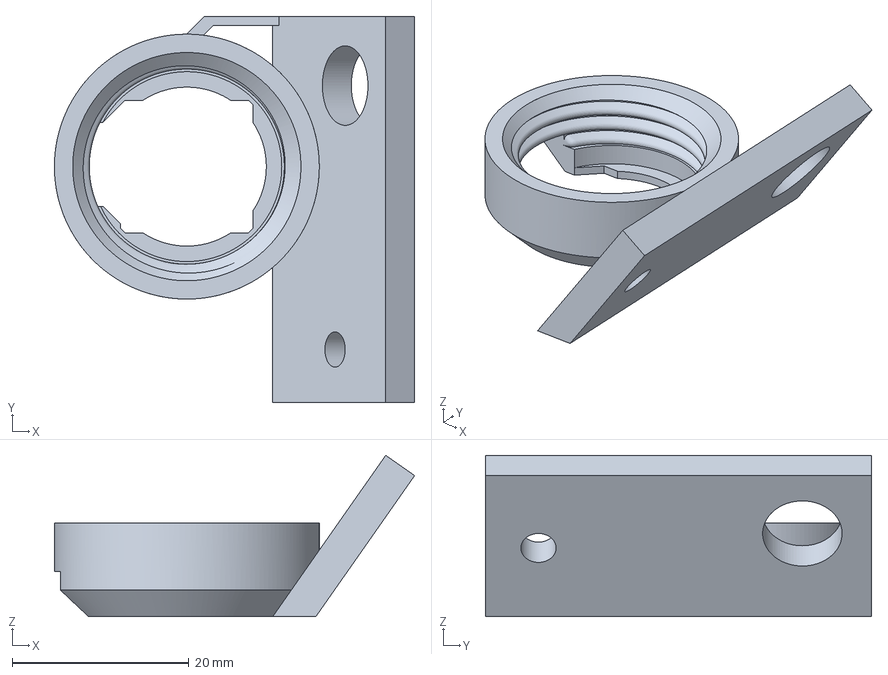
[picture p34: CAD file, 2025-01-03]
hardware/illumination/blue_light_module/Blue_LED_Holder_V1.3mf
40.8 x 43.7 x 18.3 mm

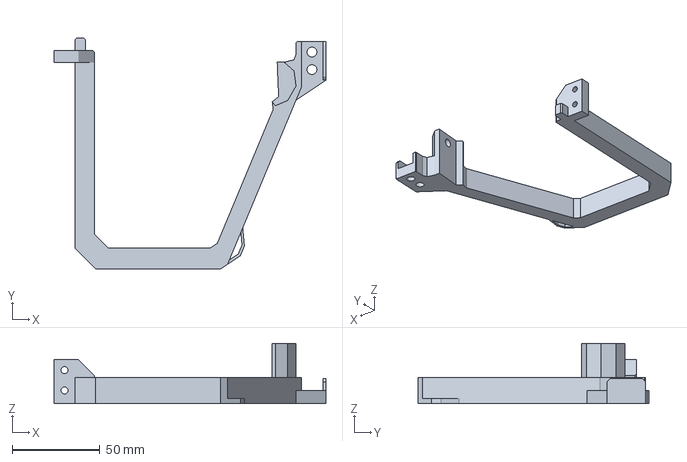
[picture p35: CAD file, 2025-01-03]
hardware/illumination/Light-Snek_V1.3mf
155.1 x 131.5 x 34.4 mm

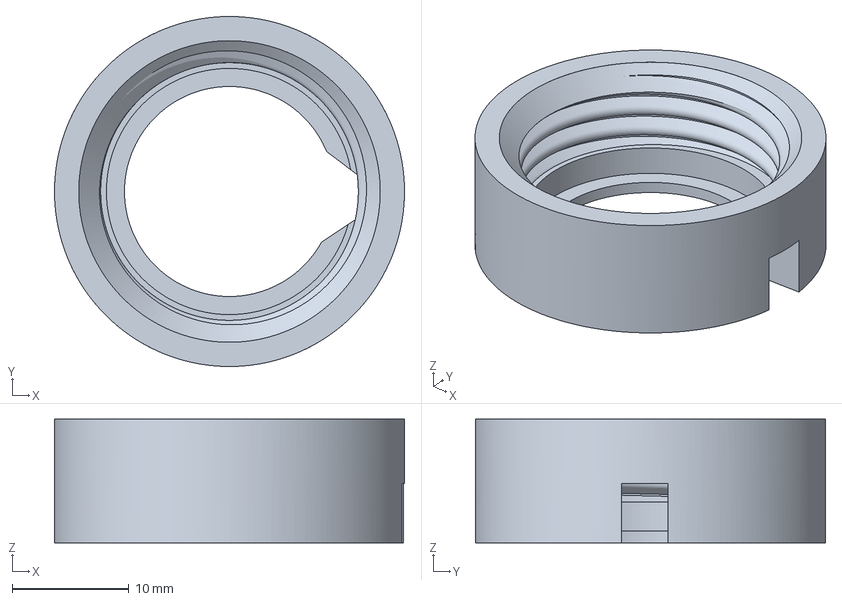
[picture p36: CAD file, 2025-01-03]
hardware/illumination/main_light_module/LED_Holder_V1.3mf
30.0 x 30.0 x 10.6 mm

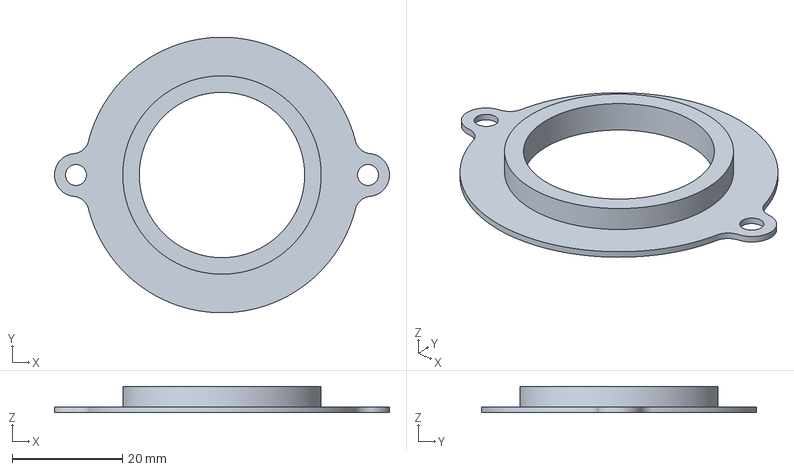
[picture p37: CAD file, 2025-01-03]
hardware/illumination/ring_light_module/Ring_light_clip_V1.3mf
60.8 x 50.0 x 4.80 mm

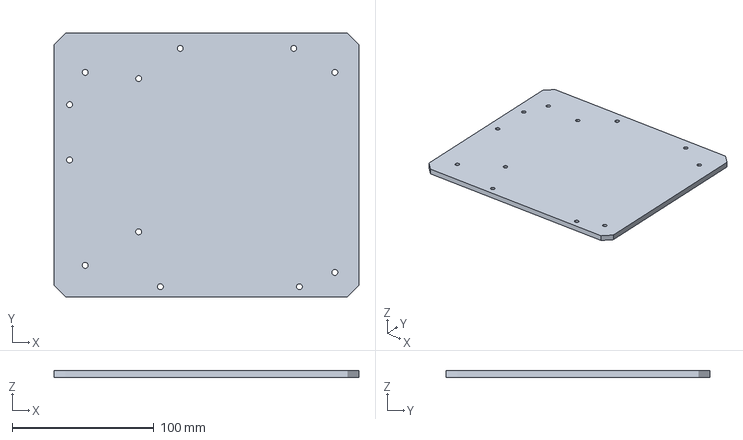
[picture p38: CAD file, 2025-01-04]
hardware/mecanical_stage/base_plate/Base_Plate_V1.3mf
215.0 x 185.8 x 5.00 mm

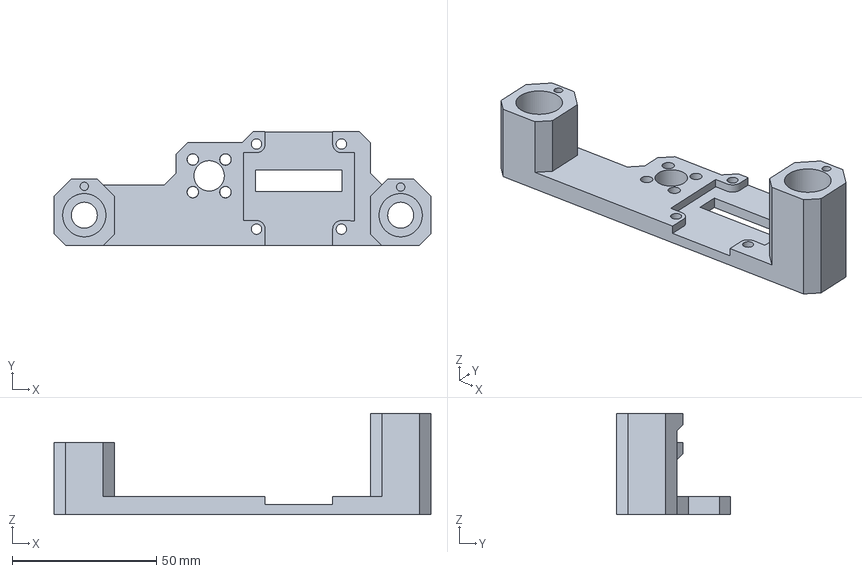
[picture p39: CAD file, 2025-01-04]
hardware/mecanical_stage/Focus_axis/Focus_Plateform_V1.3mf
130.6 x 39.5 x 35.0 mm

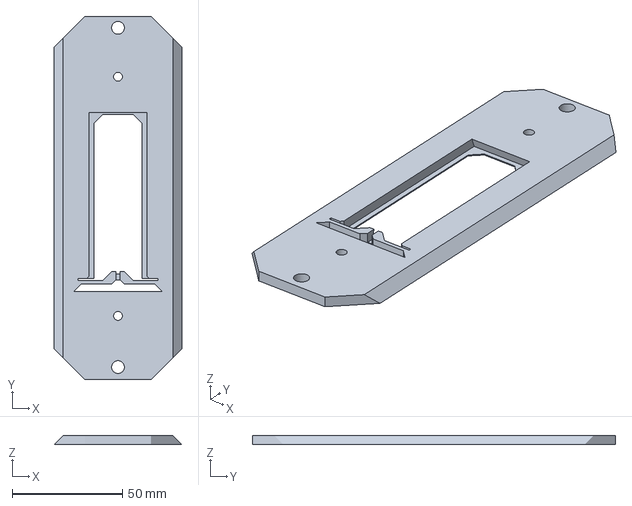
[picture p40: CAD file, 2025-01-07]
hardware/mecanical_stage/sample_holders/Slide_Holder.3mf
58.0 x 164.8 x 4.00 mm

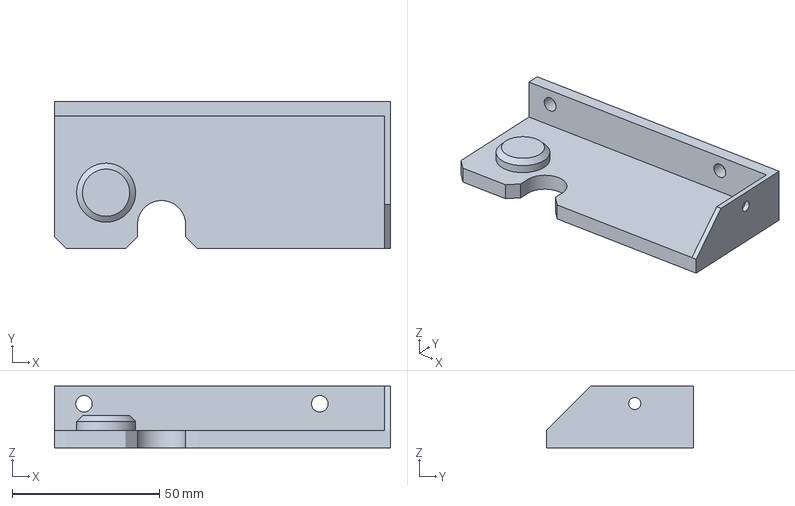
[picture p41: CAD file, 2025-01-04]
hardware/mecanical_stage/X_axis/X_back_plate_V1.3mf
114.0 x 50.0 x 21.0 mm

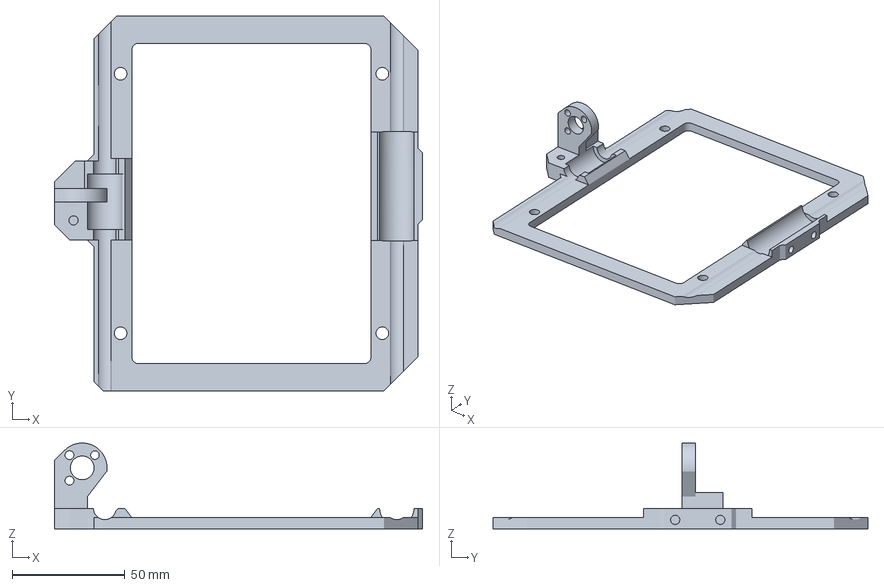
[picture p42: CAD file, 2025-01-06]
hardware/mecanical_stage/Y_axis/Y_Carriage.3mf
163.1 x 166.2 x 38.0 mm

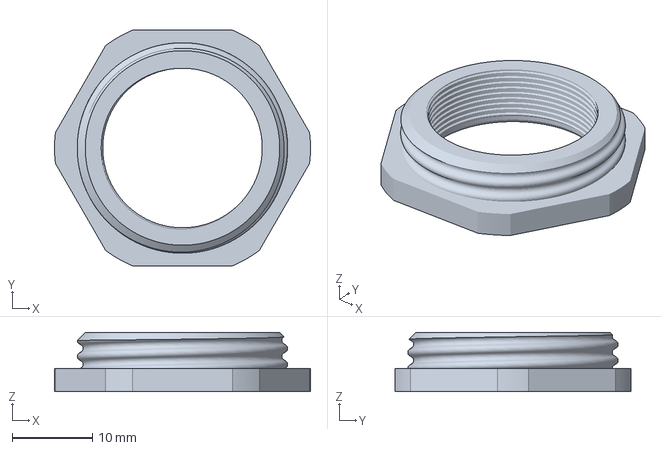
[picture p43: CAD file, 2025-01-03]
hardware/optical_stack/Lens_Adapater_V1.3mf
32.0 x 29.4 x 7.40 mm

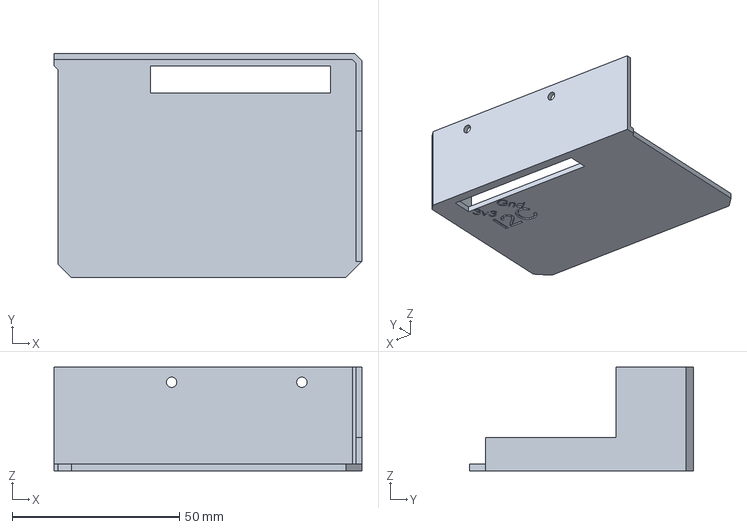
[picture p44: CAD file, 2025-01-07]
hardware/raspberryPi/PiCover_V1.3mf
92.2 x 67.0 x 31.0 mm

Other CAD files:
hardware/illumination/blue_light_module/Lens_Holder_V1.3mf
hardware/illumination/main_light_module/Condenser_lens_holder.3mf
hardware/illumination/ring_light_module/Ring_LED_Holder_V1.3mf
hardware/mecanical_stage/base_plate/Feet_V1.3mf
hardware/illumination/blue_light_module/Led_Tube_V1.3mf
hardware/illumination/main_light_module/Condenser_screw_mount_20mm.3mf
hardware/illumination/main_light_module/Led_Tube_V1.3mf
hardware/mecanical_stage/Focus_axis/Optics_Carriage_V1.3mf
hardware/mecanical_stage/X_axis/X_Side_Bar_V1.3mf
hardware/mecanical_stage/X_axis/Xmotor_Plate_V1.3mf
hardware/mecanical_stage/Y_axis/BearingClipL_V1.3mf
hardware/mecanical_stage/Y_axis/Front_Panel_V1.3mf
hardware/mecanical_stage/Y_axis/Y_Motor_Plate_V1.3mf
hardware/mecanical_stage/sample_holders/Plate_Holder_V1.3mf
hardware/optical_stack/Doublet_Holder_V1.3mf
hardware/optical_stack/Doublet_tool_V1.3mf
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

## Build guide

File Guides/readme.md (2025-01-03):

# Guides

Building guide and RaspberyPi config file

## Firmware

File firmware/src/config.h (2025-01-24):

#pragma once

//#define DEBUG_HOMING  //this will run the homing only AFTER a serial conection is detected

#define XdirPin 9
#define XstepPin 8
#define XDiagPin 6
#define XEnPin -1
#define XidxPin 7
#define X_DRIVER_ADDRESS 0b10 // TMC2209 Driver address according to MS1 and MS2
#define Xfastspd 180
#define Xslowspd 400
#define XmicroStep 8
#define XSg_sensitivity_initial 70
#define XSg_autoeval_divider 2.8  //adjust sensitivity of homing between 2 and 3 
#define X_MAX_RANGE 70000
#define X_0offset 7500 // Offset from true 0
#define X_current 900

#define YdirPin 2
#define YstepPin 3
#define YDiagPin 5
#define YEnPin -1
#define YidxPin 4
#define Y_DRIVER_ADDRESS 0b01 // TMC2209 Driver address according to MS1 and MS2
#define Yfastspd 180
#define Yslowspd 400
#define YmicroStep 8
#define YSg_sensitivity_initial 70
#define YSg_autoeval_divider 2.8 //adjust sensitivity of homing between 2 and 3 (3 = less sensitive)
#define Y_MAX_RANGE 90000
#define Y_current 1100

#define FdirPin D14
#define FstepPin 15
#define FDiagPin 16
#define FEnPin -1
#define FidxPin D13
#define F_DRIVER_ADDRESS 0b11 // TMC2209 Driver address according to MS1 and MS2
#define Ffastspd 200
#define Fslowspd 600
#define FmicroStep 8
#define FSg_sensitivity_initial 70
#define FSg_autoeval_divider 2.8 //adjust sensitivity of homing between 2 and 3
#define F_MAX_RANGE 28000
#define F_current 1000

#define Led1Pin 11
#define Led2Pin 10
#define ReadyPin 17U

#define NeoPixelPin 12
#define NeoPixelCount 16


#define R_SENSE 0.11f // Match to your driver

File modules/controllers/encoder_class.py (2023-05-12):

from RPi import GPIO

class Encoder:

    def __init__(self, clk_pin, dt_pin, pull="up", sw_pin=None, encoder_callback=None, switch_callback=None):

        ##Initiate internal states states
        self.last_state = (0,0)
        self.direction = 0
        self.sw_state = False
        self.sw_counter = 0
        self.internal_counter = 0
        
        ##callback function       
        self.encoder_callback = encoder_callback
        self.switch_callback = switch_callback

        ## Pins
        self.clk_pin = clk_pin
        self.dt_pin = dt_pin
        self.sw_pin = sw_pin
        if pull == "up":
            self.pull = True
        else:
            self.pull = False
        
        ##set pin states
        if self.pull:
            GPIO.setup(self.clk_pin, GPIO.IN, pull_up_down=GPIO.PUD_UP)
            GPIO.setup(self.dt_pin, GPIO.IN, pull_up_down=GPIO.PUD_UP)
            if sw_pin:
                GPIO.setup(self.sw_pin, GPIO.IN, pull_up_down=GPIO.PUD_UP)

        else:
            GPIO.setup(self.clk_pin, GPIO.IN, pull_up_down=GPIO.PUD_DOWN)
            GPIO.setup(self.dt_pin, GPIO.IN, pull_up_down=GPIO.PUD_DOWN)
            if sw_pin:
                GPIO.setup(self.sw_pin, GPIO.IN, pull_up_down=GPIO.PUD_DOWN)

        GPIO.add_event_detect(self.clk_pin, edge=GPIO.BOTH, callback=self.__read_state)  
        GPIO.add_event_detect(self.dt_pin, edge=GPIO.BOTH, callback=self.__read_state)
        if sw_pin:
            GPIO.add_event_detect(self.sw_pin, GPIO.RISING, callback=self.__switch_click, bouncetime=500)  

    ### End of init 

    def __switch_click(self, channel):
        self.sw_state = not self.sw_state
        self.sw_counter +=1
        if self.switch_callback:
            self.switch_callback()
    
    def __read_state(self, channel):
        
        #Generate curate state
        dt_state =  GPIO.input(self.dt_pin)
        clk_state =  GPIO.input(self.clk_pin)

        if self.pull:
            state = (not clk_state, not dt_state)
        else:
            state = (clk_state, dt_state)

    #### 00 mark the end of a turn
        if state == (0,0):
            ## check that the click is in the same direction as previous detected
            if self.last_state == (1,0) and self.direction == 1:
                self.internal_counter += 1
                if self.encoder_callback:
                    self.encoder_callback()
                self.direction = 0 ## set direction to 0 after the callback
                
            if self.last_state == (0,1)and self.direction == -1:
                self.internal_counter -= 1
                if self.encoder_callback:
                    self.encoder_callback()
                self.direction = 0 ## set direction to 0 after the callback
        
    ## Detect direction before the end of click to cross validate the click
        elif state == (0,1):
            if self.last_state == (0,0):
                self.direction = 1
            if self.last_state == (1,1):
                self.direction = -1 
        
        elif state == (1,0):
            if self.last_state == (1,1):
                self.direction = 1
            if self.last_state == (0,0):
                self.direction = -1
        
        elif state == (1,1):
            if self.last_state == (0,1):
                self.direction = 1
            if self.last_state == (1,0):
                self.direction = -1  
                
        self.last_state = state

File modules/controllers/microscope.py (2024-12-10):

# import the necessary packages
import time
from smbus2 import SMBus
import RPi.GPIO as GPIO

from modules.controllers.parametersIO import MicroscopeParameters, GridParameters
from .pins import *
from PyQt5 import QtCore
from dataclasses import dataclass
from modules.controllers import LEDArray

# Use GPIO numbers not pin numbers
GPIO.setmode(GPIO.BCM)


class Microscope:

    def __init__(self, addr, ready_pin, parameters: MicroscopeParameters):
        self.addr = addr
        self.ready_pin = ready_pin
        GPIO.setup(ready_pin, GPIO.IN) # set up the GPIO channels - one input for ready pin
        self.wait_ready()
        self.XYFposition = [0,0,0]
        self.led1pwr = 0
        self.led2pwr = 0
        self.runing = False
        self.update_real_state()
        self.parameters = parameters
        self.dynamic_endstops = False
        

        #Dynamic endsotop these will be used to modify the movement according to established safe parameters
    def set_dynamic_endsotop(self, endstops_dict):
        if endstops_dict:
            self.dynamic_endstops = True
            self.dyn_Xmax = endstops_dict["dyn_Xmax"]
            self.dyn_Xmin = endstops_dict["dyn_Xmin"]
            self.dyn_Ymax = endstops_dict["dyn_Ymax"]
            self.dyn_Ymin = endstops_dict["dyn_Ymin"]
            self.dyn_maxFcs = endstops_dict["dyn_maxFcs"]
            self.safe_Fcs = endstops_dict["safe_Fcs"]
        else:
            self.dynamic_endstops = False    

    def wait_ready(self): # wait until arduino is ready
        while not GPIO.input(self.ready_pin):  
            time.sleep(0.1)
    
    def is_ready(self): #check if arduino is ready
        return GPIO.input(self.ready_pin) 

    def send_motor_cmd(self, motor, destination):
        if destination < 0:
            destination = 0

        #Generate the message
        destination_as_bytes = int(destination).to_bytes(4, byteorder='big', signed=False)        
        checksum = (sum(destination_as_bytes)+motor) % 256
        destination_as_bytes += bytes([checksum])
                
        i=0
        while i <= retry: #do the comunication, but catch error and retry in case of problem
            try:
                with SMBus(1) as bus: #open I²C bus, and do the proper comunication
                    bus.write_i2c_block_data(self.addr, motor, destination_as_bytes)
            except:
                time.sleep(1)
                i=i+1
                print("At "+ time.strftime("%H:%M:%S", time.localtime()) +" motor comunication error, retrying "+str(i)+" of "+ str(retry) +" times")
            else:
                break

        if i > retry:
                print("At "+ time.strftime("%H:%M:%S", time.localtime()) + "motor comunication error, exit after "+str(i)+"retry")
                exit()

    def push_axis(self, motor, amount):
        with SMBus(1) as bus: #open I²C bus, and do the proper comunication
            #bus.write_i2c_block_data(self.addr, motor + 10, 100)
            #bus.write_byte_data(self.addr, motor + 0x10, amount)

            steps = abs(amount)
            if amount > 0:
                cmd =  motor + 0x10
            else:
                cmd =  motor + 0x20
            if steps > 255:
                steps = 255
            data = bytes([steps, steps])
            bus.write_i2c_block_data(self.addr, cmd, data)

    def move_single_axis(self, motor, destination):
        i = 1
        while i <= retry:

            destination = self.make_safe(motor, destination)

            if not self.is_ready():
                return False

            if self.XYFposition[motor-1] == destination:
                return True
            
            self.send_motor_cmd(motor, destination)
            return True

    def move_focus(self, destination):
        F_done =self.move_single_axis(3, destination)
        return F_done
    
    def move_X_Y(self, destination_X, destination_Y):

        X_done = self.move_single_axis(1,destination_X)
        Y_done = self.move_single_axis(2,destination_Y)
        return X_done , Y_done

    def make_safe(self, motor, destination): #Software and dynamic endstops, update destination to avoid collision or out of range

        if destination < 0:
            return 0
        
        if self.parameters.software_endstops:
            if motor == 1 and destination > self.parameters.Xmaxrange:
                destination = self.parameters.Xmaxrange            
            if motor == 2 and destination > self.parameters.Ymaxrange:
                destination = self.parameters.Ymaxrange
            if motor == 3 and destination > self.parameters.Fmaxrange:
                destination = self.parameters.Fmaxrange   
        

        #Dynamic endstops should be used to delimite a safe area coresponding to the observation window
        if self.dynamic_endstops:

            if self.XYFposition[2] >= self.safe_Fcs: ### Stop movement if the objective is to close to unsafe borders
                
                if motor == 1 and destination < self.dyn_Xmin:
                    destination = self.dyn_Xmin
                if motor == 1 and destination >  self.dyn_Xmax:
                    destination = self.dyn_Xmax
                
                if motor == 2 and destination <  self.dyn_Ymin:
                    destination = self.dyn_Ymin
                if motor == 2 and destination >  self.dyn_Ymax:
                    destination = self.dyn_Ymax
            
            if motor == 3 and destination > self.dyn_maxFcs:
                destination = self.dyn_maxFcs   
             
            if motor == 3 and destination > self.safe_Fcs and (self.XYFposition[0] < self.dyn_Xmin or self.XYFposition[0] > self.dyn_Xmax or 
                                                            self.XYFposition[1] >  self.dyn_Ymax or self.XYFposition[1] < self.dyn_Ymin ):
                destination = self.safe_Fcs
            
        return destination
        
    def go_absolute(self, destinations: list[int,int,int]): #ordered movement of the 3 axis, move focus first of last depending on condition to avoid triggering dyn_endstop
        if destinations[2] < self.XYFposition[2]: #move focus first if it's going down (park)
            F_done = self.move_focus(destinations[2]) 
            X_done , Y_done =self.move_X_Y(destinations[0],destinations[1])
        else: #move focus last if it's going up (start)
            X_done , Y_done = self.move_X_Y(destinations[0],destinations[1])    
            F_done = self.move_focus(destinations[2])

        return all([F_done, X_done , Y_done])  # return false if any is false
   
    def set_ledspwr(self, led1pwr, led2pwr):
        with SMBus(1) as bus:
            checksum = (led1pwr + led2pwr) % 256 
            bus.write_i2c_block_data(addr, 4, [ 4 , led1pwr, led2pwr,checksum])
            self.led1pwr = led1pwr
            self.led2pwr = led2pwr

    def send_simplecmd(self, cmd):
        with SMBus(1) as bus:
            bus.write_byte_data(addr, cmd, cmd) #command need to be sent twice to be executed (crude error check)
         
    def read_positions(self): #get position from the microscope   
        try:  # Read 15 bytes (last is checksum)
            with SMBus(1) as bus:
                msg = bus.read_i2c_block_data(addr, 0, 15) #generate I²C msg instance as msg
                
        except:
            time.sleep(0.5)
            print("At "+ time.strftime("%H:%M:%S", time.localtime()) +" read position: comunication error")                   
            return False
        
        checksum = (sum(msg[:14])) %256 
        if checksum != msg[14]:
            return False
        
        #generate integer from the list of bytess.
        
        X_pos = int.from_bytes(msg[:4], byteorder='little', signed=False)
        Y_pos = int.from_bytes(msg[4:8], byteorder='little', signed=False)
        Focus_pos = int.from_bytes(msg[8:12], byteorder='little', signed=False)		
        led1 = msg[12]
        led2 = msg[13]

        positions = [X_pos, Y_pos, Focus_pos, led1, led2]
        return positions

    def update_real_state(self): #return position if read_postiions() is not none (=checksum match) or exit after 10 retry
        positions = self.read_positions()
        if positions:
            self.XYFposition = positions[:3]
            self.led1pwr = positions[3]
            self.led2pwr = positions[4]
            return True
        else:
            return False
    
    def adressable_LED_solid_color(self, R,G,B):
            checksum = (R + G +B ) % 256 
            with SMBus(1) as bus:
                bus.write_i2c_block_data(addr, 5, [ 5 , R, G, B, checksum])

    def adressable_LED_indexLed(self, index, R,G,B):

        checksum = (index + R + G +B ) % 256 
        with SMBus(1) as bus:
            bus.write_i2c_block_data(addr, 6, [ 6 ,index, R, G, B, checksum])
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

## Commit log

2023-09-05 new fluorescent filtering
2023-09-11 changed image capture thread to cv2
2023-09-18 camera control as object
2023-09-19 debugging new cameracontrol module
2024-12-18 Add Samples to repository
2025-01-03 Initial upload optical stack
    [Doublet_Holder_V1.3mf, Doublet_tool_V1.3mf, Lens_Adapater_V1.3mf, Main_Tube_V1.3mf]
2025-01-03 added files for the illumination
    [Condenser_lens_holder.3mf, Condenser_screw_mount_20mm.3mf, LED_Holder_V1.3mf, Led_Tube_V1.3mf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]
2025-01-03 added blue led files
    [Blue_LED_Holder_V1.3mf, Led_Tube_V1.3mf, Lens_Holder_V1.3mf]
2025-01-03 Electronic board upload
2025-01-03 typo in folder name
    [Blue_LED_Holder_V1.3mf, Condenser_lens_holder.3mf, Condenser_screw_mount_20mm.3mf, Doublet_Holder_V1.3mf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]
2025-01-04 Reorganise and added X and F axis
    [Base_Plate_V1.3mf, Blue_LED_Holder_V1.3mf, Condenser_lens_holder.3mf, Condenser_screw_mount_20mm.3mf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]
2025-01-04 added the printable files
    [Focus_Plateform_V1.3mf, Optics_Carriage_V1.3mf]
2025-01-06 added Bracket to electronics
    [Electronic_Bracket_V1.3mf]
2025-01-06 Added Y
    [BearingClipL_V1.3mf, Front_Panel_V1.3mf, Y_Carriage.3mf, Y_Motor_Plate_V1.3mf]
2025-01-07 added RPi stuff
    [PiCover_V1.3mf, Pi_Bracket_V1.3mf]
2025-01-07 Update electronic descritpiton
    [Plate_Holder_V1.3mf, Slide_Holder.3mf]
2025-01-10 change vrm reference for pcb 1.3
2025-01-24 addapt to board 1.2
